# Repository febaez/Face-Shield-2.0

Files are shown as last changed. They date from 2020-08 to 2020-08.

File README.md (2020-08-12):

# Face-Shield-2.0

## Tabla de contenidos 
- [Face Shield 2.0](#face-shield-2.0)
    + [Tabla de contenidos](#tabla-de-contenidos)
  * [Resumen](#resumen)
  * [Primera versión](#primera-versi-n)
  * [Partes](#partes)
    + [Partes impresas](#partes-impresas)
      - [Cintillo fijo impreso en 3D](#cintillo-fijo-impreso-en-3d)
      - [Parte móvil impresa en 3D](#parte-m-vil-impresa-en-3d)
      - [Parte elástica impresa en 3D](#parte-el-stica-impresa-en-3d)
      - [Impresión de piezas](#impresi-n-de-piezas)
    + [Partes comerciales](#partes-comerciales)  
      - [Mica tamaño oficio](#mica-tamaño-oficio) 
      - [Elástico común](#el-stico-com-n)
  * [Ensamble](#ensamble)

## Resumen
Este dispositivo nace dentro del contexto Covid 19 para satisfacer la necesidad de equipos médicos de poder levantar el escudo facial sin la necesidad de sacarlo para realizar labores como: comer, tomar agua, o tener mejores perspectivas visuales dentro de su turno de trabajo.

## Primera versión
Ya se encuentra disponible la primera versión de este escudo facial.  

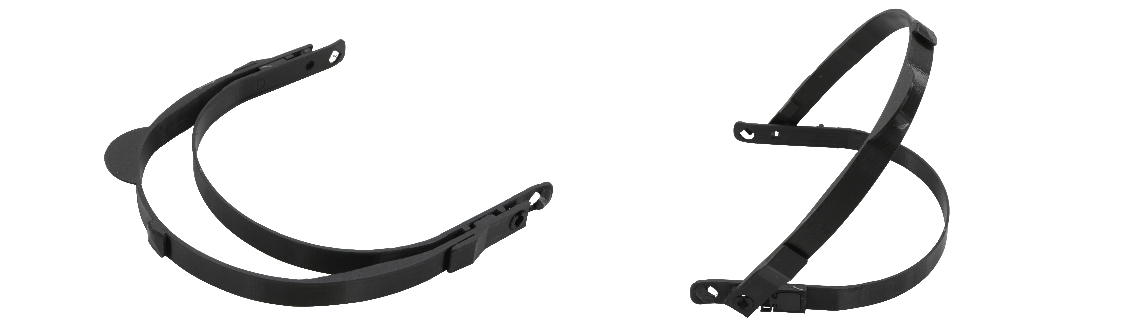
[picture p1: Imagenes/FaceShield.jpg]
FaceShield


## Partes 

El escudo facial esta compuesto por 5 componentes:
* Cintillo fijo impreso en 3D. 
* Parte móvil impresa en 3D.
* Parte elástica impresa en 3D.
* Lámina transparente de acetato de celusosa (mica tamaño oficio (216x356mm)).
* Elástico común.

### Partes impresas
Puedes descargar los archivos .STL o .STP de las piezas que se muestran a continuación en [Grabcad](https://grabcad.com/library/face-shield-2-0-2).
#### Cintillo fijo impreso en 3D
Esta pieza consiste en una banda con ganchos en sus extremos para colocar un elástico, o sistema similar, que permita ajustar el cintillo en la cabeza. Además, en ambos extremos posee pasadores para poder colocar la parte móvil del escudo facial, en su lado derecho posee un soporte para colocar la pieza elástica y por último en su lado izquierdo cuenta con un tope para impedir que la parte móvil baje más de lo requerido. 

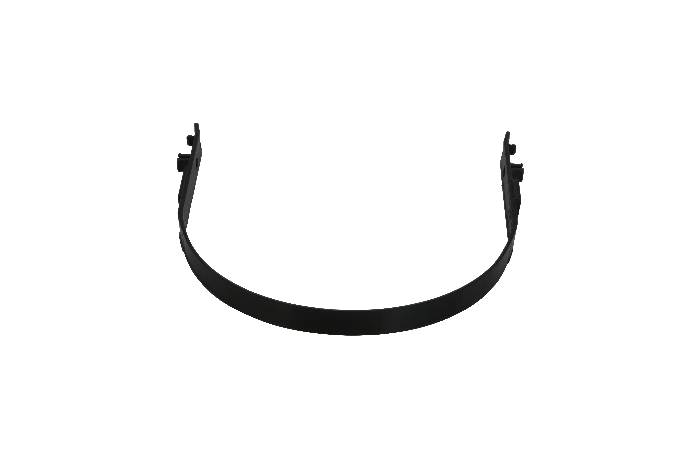
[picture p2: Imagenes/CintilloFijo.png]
CintilloFijo


#### Parte móvil impresa en 3D
Esta pieza consiste en cintillo con tres solapas en su parte frontal para poder colocar la mica, también posee una solapa grande con la cual se puede mover la parte móvil. Asimismo, en sus extremos, esta pieza cuenta con orificios para poder ensamblarla mediante pasadores en la parte fija; en su lado derecho posee una especie de engranaje que permite, en conjunto con la parte elástica, que la pieza quede fija en cada una de las posiciones y en su lado izquierdo tiene partes que conforman el sistema para que este cintillo no baje más de lo necesario.   

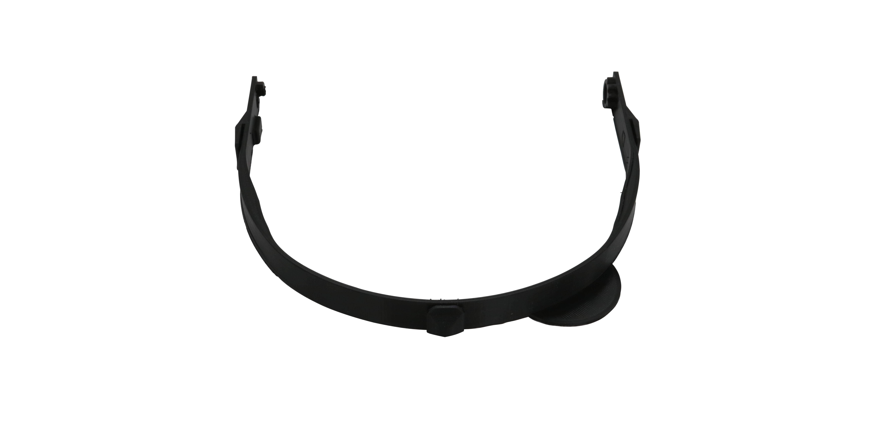
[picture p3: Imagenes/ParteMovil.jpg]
ParteMovil


#### Parte elástica impresa en 3D
Esta pieza consta de una parte mediante la cual se fija al cintillo fijo y una parte que, debido a su geometría, es capaz de comprimirse y luego volver a su forma original. Esto último es lo que permite que la parte móvil pueda moverse y permanecer fija en las diferentes posiciones.

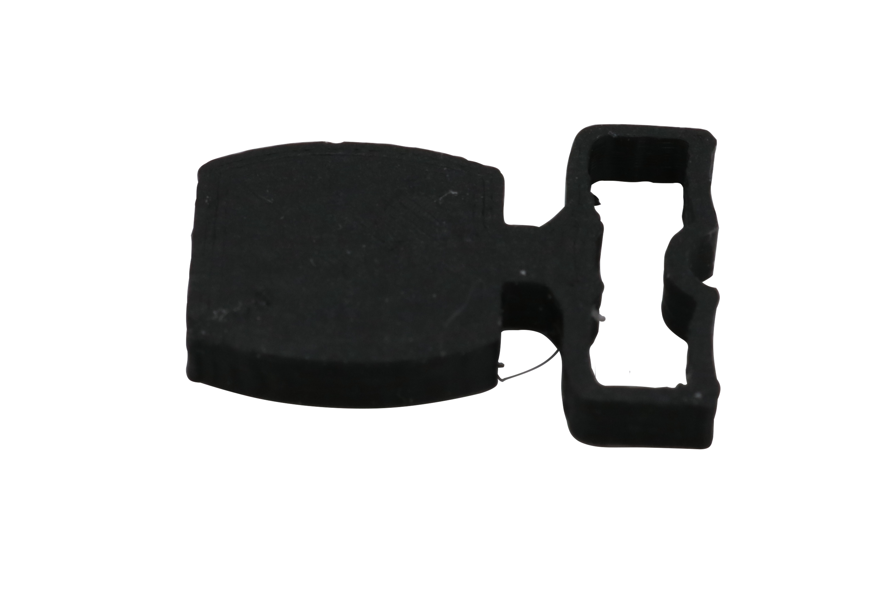
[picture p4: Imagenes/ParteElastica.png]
ParteElastica


#### Impresión de piezas
Para imprimir las partes o piezas mencionadas te recomendamos orientarlas como se observa en la siguiente imagen:

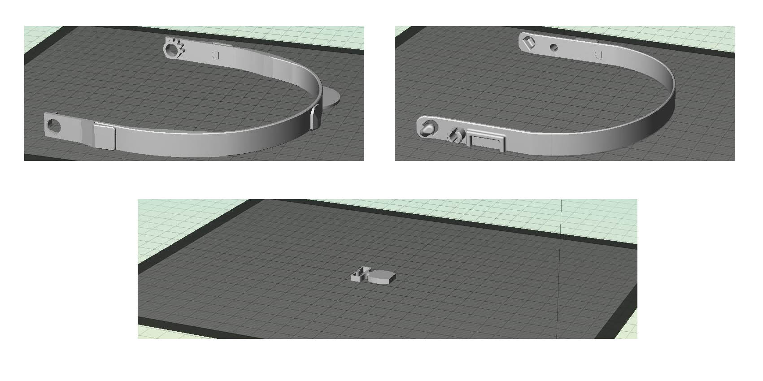
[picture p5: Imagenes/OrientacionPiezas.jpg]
OrientacionPiezas


Asimismo, te recomendamos utilizar los siguientes parámetros de impresión:
* Material: PLA
* Temperatura de extrusor: 210ºC
* Temperatura cama: 50ºC
* Altura capa: 0.2 mm
* Número de Shells: 3
* Infill: 10%
* Velocidad de impresión: 30 mm/s infill, 15 mm/s shell

### Partes comerciales
#### Mica tamaño oficio 
La lámina de mica es de tamaño oficio (216x356 mm) y debe ser posicionada de forma horizontal para así brindar la mayor protección posible.

#### Elástico común
Para fijar la parte móvil a tu cabeza puedes ocupar un elástico común o cualquier elástico que te acomode. 
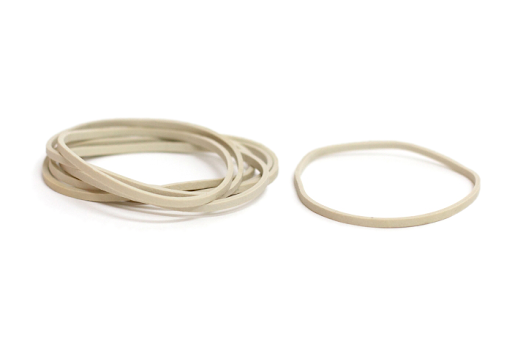
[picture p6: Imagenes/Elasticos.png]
Elasticos


## Ensamble 
Una vez que cuentes con todas las partes que coforman al escudo facial debes seguir los siguientes pasos para realizar su ensamble:

1. Inserta la parte elástica en el soporte que el cintillo posee para la misma.

2. Coloque la parte móvil en el cintillo insertando los pasadores por los agujeros en el extremo del cintillo móvil. 

3. Ubique la mica en forma horizontal e inserte las esquinas superiores y la parte de en medio de la misma en las solapas de la parte móvil.

4. Coloque el elástico, o sistema que le acomode, en los ganchos que posee el cintillo en sus extremos.

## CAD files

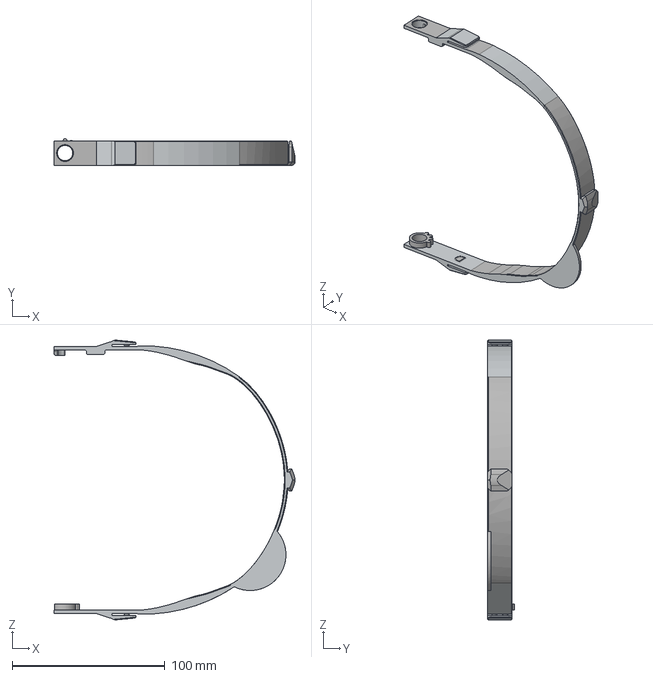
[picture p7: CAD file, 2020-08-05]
Archivos CAD/STEP/ParteMovil.stp
157.7 x 17.4 x 183.3 mm

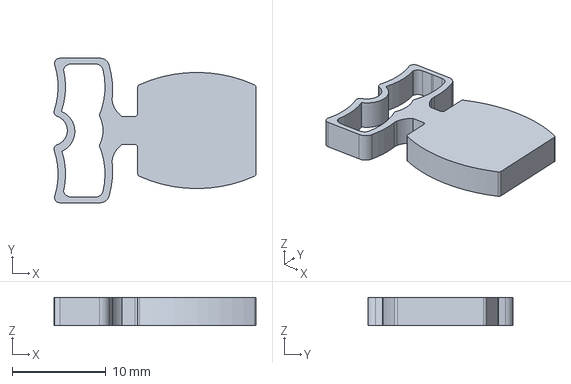
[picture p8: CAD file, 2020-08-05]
Archivos CAD/STEP/ParteElastica.stp
21.5 x 15.4 x 3.00 mm

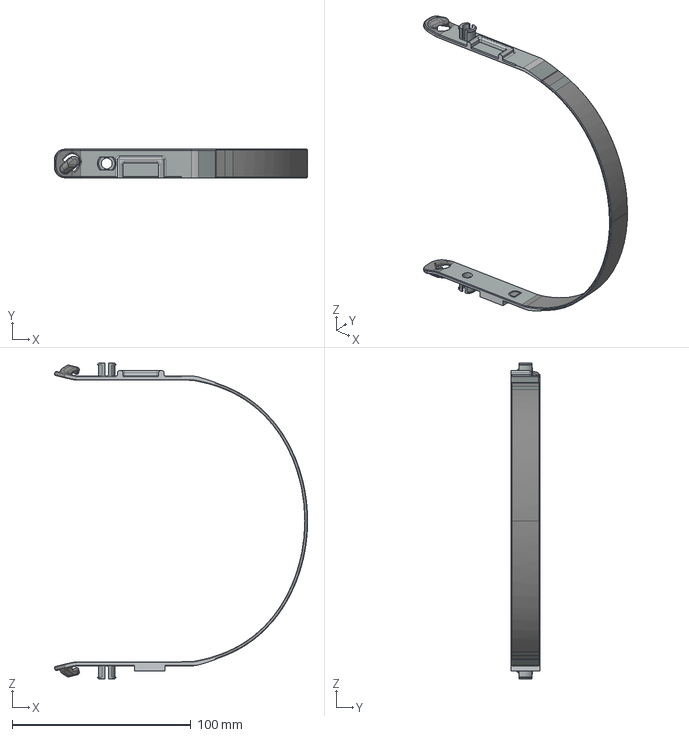
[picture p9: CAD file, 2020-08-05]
Archivos CAD/STEP/ParteFija.stp
141.5 x 16.0 x 176.6 mm

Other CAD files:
Archivos CAD/STL/ParteElastica.stl

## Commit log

2020-08-05 modificaciones
    Se agregan imagenes, archivos step y stl y se edita archivo readme.
    [ParteElastica.stl, ParteElastica.stp, ParteFija.stp, ParteMovil.stp]
2020-08-12 se agrega imagen orientación piezas
    Agrego imagen con la orientación de las piezas para su impresión
